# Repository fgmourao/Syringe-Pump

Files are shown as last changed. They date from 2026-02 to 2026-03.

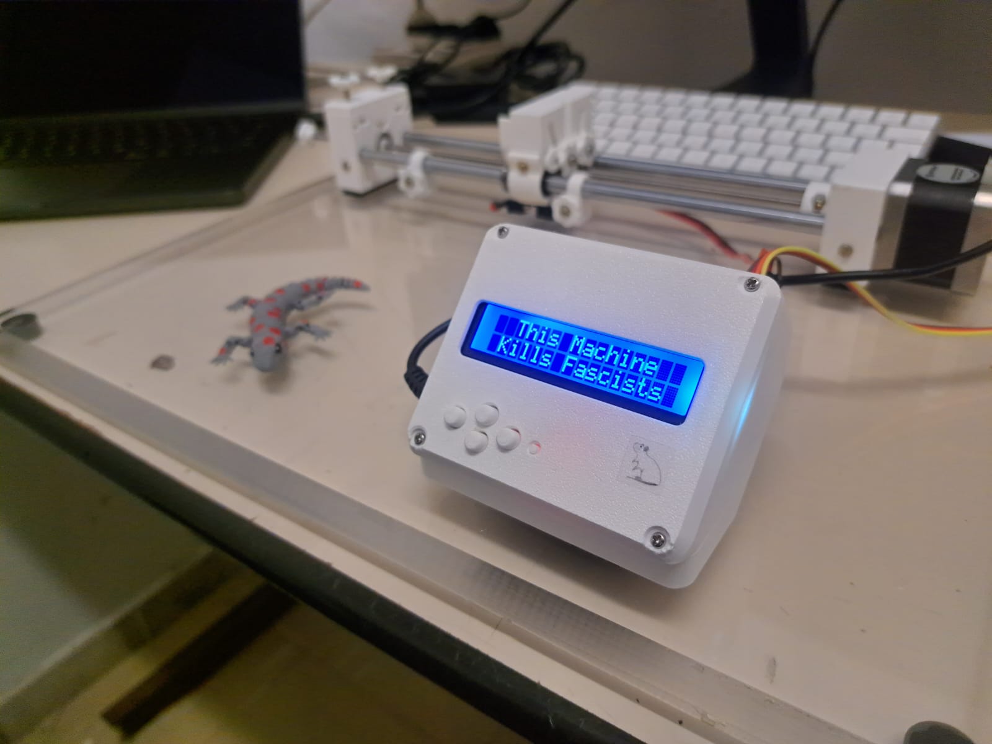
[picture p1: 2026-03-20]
Images/3.jpeg

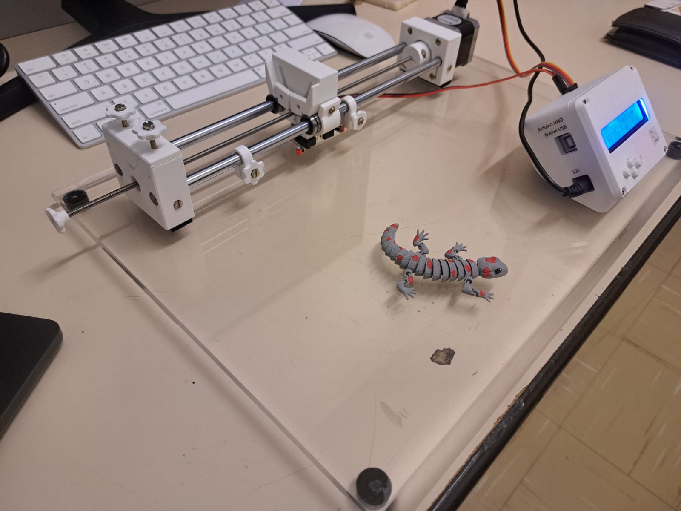
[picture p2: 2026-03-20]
Images/1.jpeg

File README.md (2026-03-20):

# Open-Source Syringe Pump – Modified Version

This firmware is a modified version of the open-source syringe pump originally developed by **Andrey Samokhin** (v0.9a, March 1, 2020).

> **Original project:** [mass-spec.ru/projects/diy/syringe_pump/eng](https://www.mass-spec.ru/projects/diy/syringe_pump/eng/)
> *All credit for the original concept and baseline implementation belongs to the original author.*

The modifications listed below were made targeting improved motion smoothness, manual positional control, and operator safety during microinjection procedures.

Updated: 01/2026 by Flavio Mourao

---

## Change 1 — Lead screw pitch updated

The default lead screw was replaced with a **0.6 mm/revolution** unit, reducing linear displacement per motor step and resulting in smoother, more continuous motion during fine procedures.

| Parameter | Original | Modified |
| :--- | :---: | :---: |
| Lead screw pitch | 2.0 mm/rev | **0.6 mm/rev** |

---

## Change 2 — Manual Positioning Mode (Jog Control)

A dedicated **Positioning** entry was added to the main menu (between *Cycle Mode* and *Settings*), enabling direct real-time control of the syringe position via the existing interface buttons.

### Button mapping

| Button | Action |
| :--- | :--- |
| **UP** | Forward movement (while held) |
| **DOWN** | Backward movement (while held) |
| **LEFT** | Exit positioning mode |
| **RIGHT** | Reset relative position counter ($mm = 0$) |

### Features
* **Press-to-move:** Movement occurs only while a button is actively held.
* **Dual-speed operation:** short press → fine positioning; long press → fast positioning.
* **Power efficiency:** Stepper driver is enabled only during active movement, reducing heat and electrical noise.
* **Endstop safety:** Audible beep when a mechanical limit is reached; movement stops automatically.
* **Real-time feedback:** Relative displacement displayed in millimeters on the LCD.

> **Note:** This mode is intended for manual syringe alignment and fine adjustment prior to automated infusion.

---

## Change 3 — Startup screensaver customized

---

## Change 4 — Start confirmation dialog added

A `confirmStart()` function was introduced to require explicit operator confirmation before any pumping operation begins. After selecting an infusion or refill action, the LCD prompts:

```
Ready to Start?
< NO       YES >
```

* **RIGHT** → confirm and proceed
* **LEFT** → cancel and return to menu

---

## Change 5 — Rounding correction in value calculation

In the original `calculateActualValue()` function, the computed
FLOWRATE and VOLUME values were assigned to `uint32_t` via direct
float-to-integer cast, which always truncates (e.g. `2.9 → 2`).

This was replaced with conventional rounding by adding `0.5` before
the cast (e.g. `(uint32_t)(value + 0.5)`), consistent with the
rounding already applied elsewhere in the original code.

| Location | Original | Modified |
| :--- | :--- | :--- |
| FLOWRATE assignment | `(uint32_t)tempFloat` | `(uint32_t)(tempFloat + 0.5)` |
| VOLUME assignment | `(uint32_t)tempFloat` | `(uint32_t)(tempFloat + 0.5)` |

This reduces cumulative rounding errors in microstep counts,
improving dispensed volume accuracy over repeated operations.

---

## Summary

| # | Change | Scope |
| :---: | :--- | :--- |
| 1 | Lead screw pitch: 2.0 → 0.6 mm/rev | Mechanical + firmware (`MMPER360`) |
| 2 | Manual Positioning Mode (jog control) | Firmware — new function + menu entry |
| 3 | Custom startup screensaver | Firmware — `showScreensaver()` |
| 4 | Start confirmation dialog | Firmware — new `confirmStart()` + `pumpSingly()` |
| 5 | Rounding correction in value calculation | Firmware — `calculateActualValue()` |

---

## Author

Flavio Mourao (mourao.fg@gmail.com)  
Federal University of Minas Gerais, Brazil  

Development started: January 2026  
Last update: March 2026

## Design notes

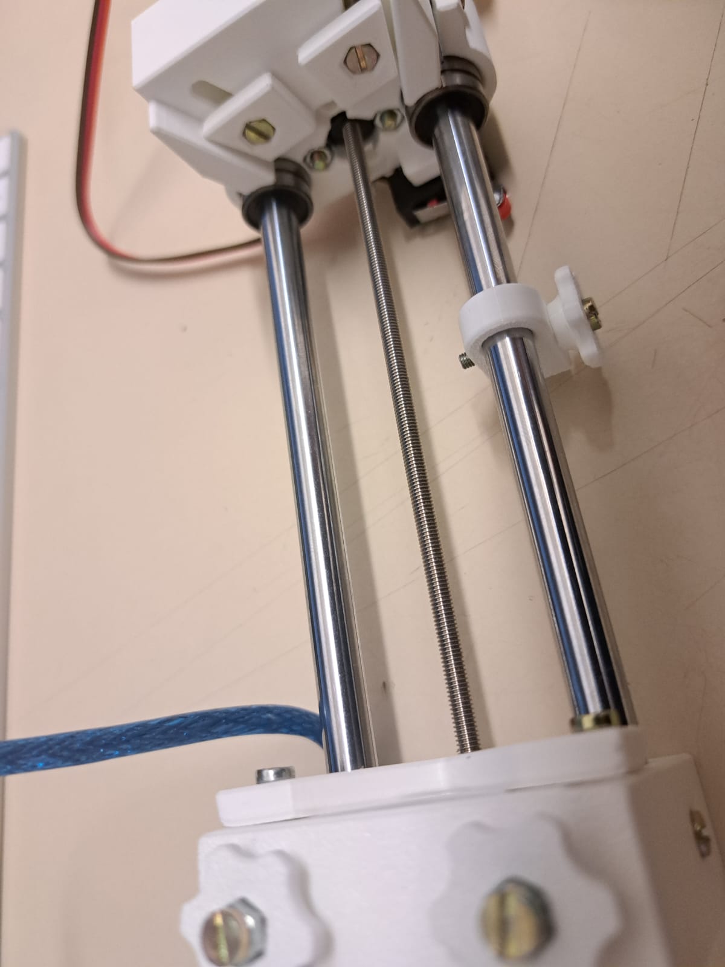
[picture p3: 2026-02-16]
Images/lead_screw_0-6mm.jpeg

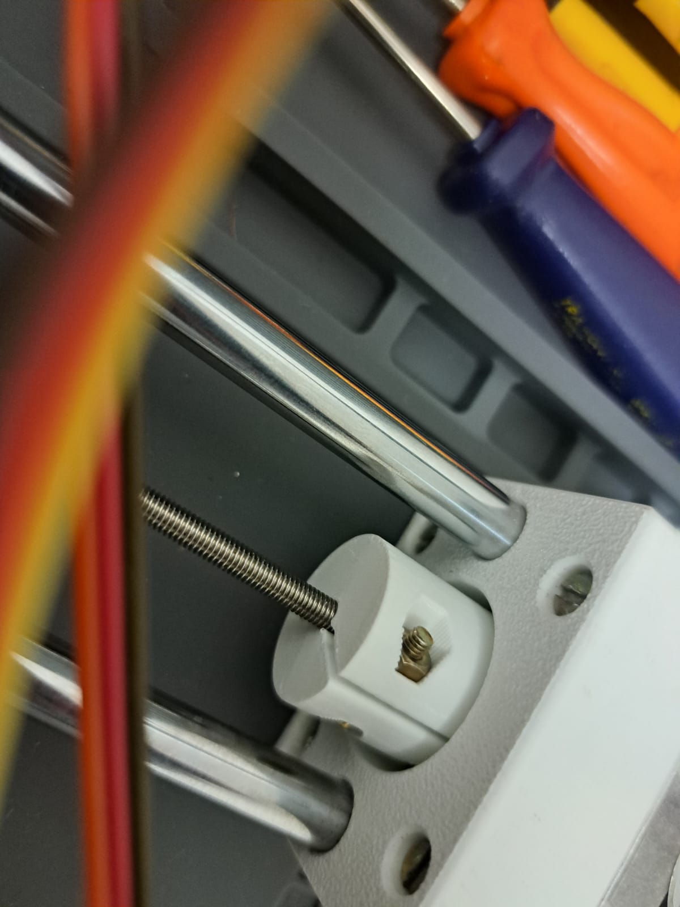
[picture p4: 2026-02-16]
Images/lead_screw_holder_0-6mm.jpeg

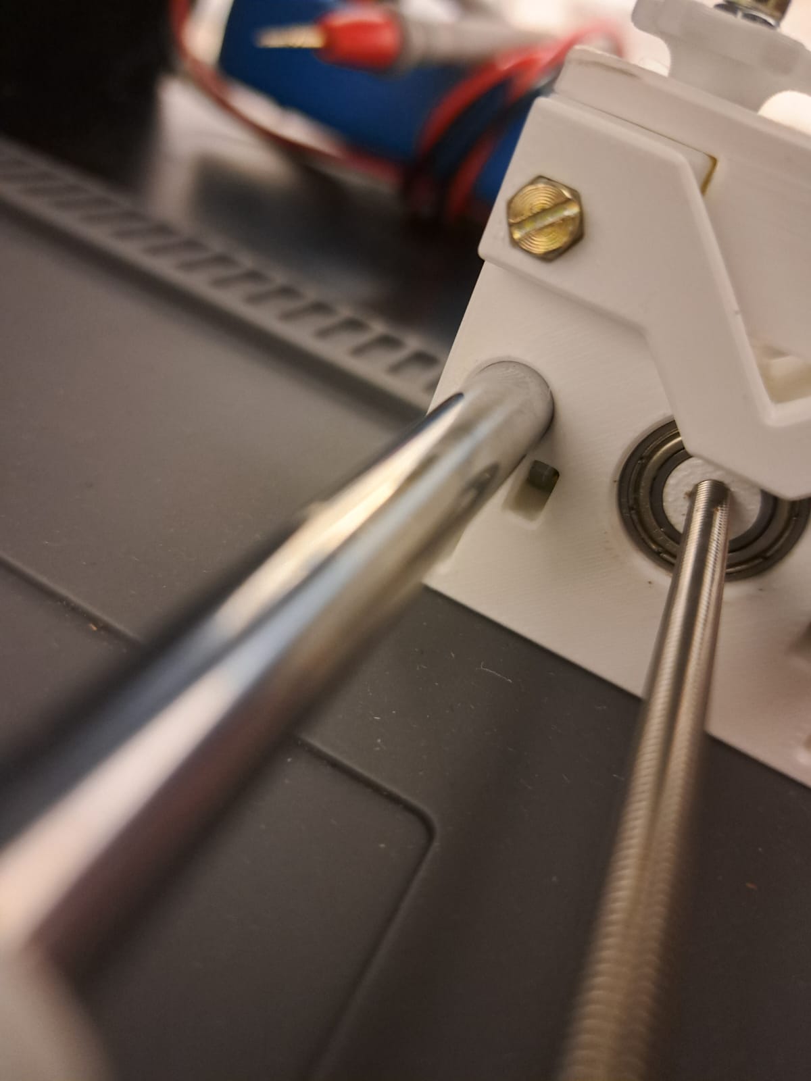
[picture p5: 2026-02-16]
Images/lead_screw_front_adapt.jpeg

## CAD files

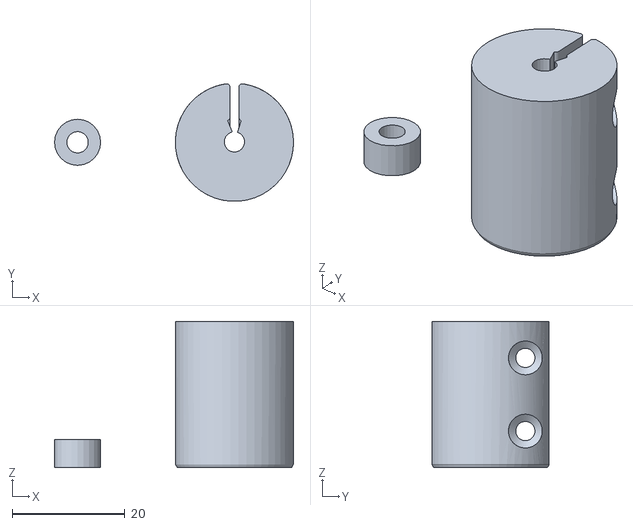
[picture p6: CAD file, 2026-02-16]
3D_/Updates/Flavio_update_adapters_0-6_step_fuse.stl
42.5 x 20.9 x 26.0

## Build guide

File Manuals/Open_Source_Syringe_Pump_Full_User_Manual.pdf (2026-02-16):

# Open-Source Syringe Pump User Manual

Based on the original project by Andrey Samokhin (2020).
Firmware updates and mechanical modifications by Flavio Mourão (2026).

## 1. Overview

This open-source syringe pump is designed for precise liquid delivery and withdrawal, with particular emphasis on laboratory microinjection applications. The system integrates automated pumping modes with a manual positioning (jog) mode, providing both reproducibility and fine user control.

## 2. Hardware Configuration

### Stepper Motor and Drive

The system uses a 200 steps/revolution stepper motor with 16× microstepping, driven by an A4988-compatible driver. The maximum operational speed is 240 RPM.

### Lead Screw

A lead screw with a 0.6 mm/revolution lead was incorporated into the original design to reduce linear displacement per motor step. This modification results in smoother motion and improved controllability during microinjection, while preserving the intrinsic precision of the stepper motor system.

### Endstops

Two mechanical endstops are installed to define the forward (syringe empty) and backward (syringe full) limits, providing hardware-level protection against overtravel.

## 3. User Interface

### Display

A 16×2 LCD is used to display menus, parameters, and real-time operational status.

### Buttons (LCD Keypad Shield)

UP: Navigate up / Forward jog (Positioning mode)
DOWN: Navigate down / Backward jog (Positioning mode) LEFT: Navigate back / Exit positioning mode
RIGHT: Navigate forward / Reset position (Positioning mode) SELECT: Confirm menu item / Edit values

## 4. Menu Structure

Main menu items include: Infuse, Refill, Cycle Mode, Settings, and Positioning.

## 5. Automated Pumping Modes

Infuse Volume: Delivers a defined volume at a specified flow rate. Infuse Time: Infuses continuously for a defined duration.
Refill Volume: Withdraws a defined volume at a specified flow rate. Full Refill: Withdraws until the backward endstop is reached. Cycle Mode: Alternates between infusion and refill automatically.

## 6. Manual Positioning Mode (Jog Control)

The Positioning mode is intended for syringe alignment, manual calibration, and fine positioning prior to microinjection procedures.

### Controls

UP: Forward movement (while pressed) DOWN: Backward movement (while pressed) LEFT: Exit positioning mode
RIGHT: Reset position to zero (mm = 0)

### Behavior

Movement occurs only while a button is pressed; releasing the button immediately stops the motor. Two speeds are automatically selected based on press duration: short press for fine positioning and long press for fast movement.

### Position Display

The LCD displays the relative linear displacement in millimeters in real time. The position is relative and can be reset at any time using the RIGHT button.

### Endstop Feedback

When a mechanical endstop is reached, motion stops immediately and an audible beep is emitted to notify the user.

## 7. Safety Notes

Always verify syringe parameters before operation. Manual positioning should be performed at low speed near the end of travel. Mechanical endstops provide the primary safety mechanism against overtravel.

## 8. Intended Use

This device is intended for laboratory research applications, including microinjection and controlled fluid delivery. It is not certified for clinical or medical use.

## 9. Version Information

Firmware version: 0.9a
Original project: Andrey Samokhin (2020)
Firmware extensions and mechanical updates: Flavio Mourão (2026)

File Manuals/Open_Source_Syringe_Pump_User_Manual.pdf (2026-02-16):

# Open-Source Syringe Pump – User Manual

Based on the original project by Andrey Samokhin (2020). Firmware updates and mechanical modifications by Flavio Mourão (2026).

## Overview

This open-source syringe pump is designed for precise fluid delivery and withdrawal, with special emphasis on microinjection applications. The system integrates automated pumping modes with a manual positioning (jog) mode.

## Mechanical Configuration

A lead screw with a 0.6 mm/revolution lead was incorporated into the original design to reduce linear displacement per motor step, resulting in smoother motion during microinjection, while preserving the intrinsic precision of the stepper motor system.

## Manual Positioning Mode (Jog Control)

The Positioning mode is intended for syringe alignment, fine manual adjustment, and preparation prior to microinjection procedures.
Controls:
UP: Forward movement (while pressed)
DOWN: Backward movement (while pressed) LEFT: Exit positioning mode
RIGHT: Reset position to zero (mm = 0)

## Features

- Movement occurs only while a button is pressed
- Two automatic speeds (short press = fine, long press = fast)
- Stepper driver enabled only during motion
- Audible feedback when a mechanical endstop is reached
- Real-time display of relative displacement in millimeters

## Safety Notes

Mechanical endstops provide hardware-level protection against overtravel. Manual positioning should be performed carefully near the end of syringe travel.

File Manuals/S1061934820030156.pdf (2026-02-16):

ISSN 1061-9348, Journal of Analytical Chemistry, 2020, Vol. 75, No. 3, pp. 416–421. © Pleiades Publishing, Ltd., 2020. Russian Text © The Author(s), 2020, published in Zhurnal Analiticheskoi Khimii, 2020, Vol. 75, No. 3, pp. 281–287.

## Syringe Pump Created Using 3D Printing Technology and Arduino Platform

A. S. Samokhin*
Lomonosov Moscow State University, Chemistry Department, Moscow, 119991 Russian *e-mail: andrey.s.samokhin@gmail.com

Received December 24, 2018; revised September 1, 2019; accepted September 1, 2019

Abstract—An open-source syringe pump has been developed for use in the analytical laboratory. Most pump parts are made on a 3D printer. Other parts (lead screw, guide rods, stepper motor, bearings, electronic components) are purchased in specialized stores. The control panel is based on the Arduino UNO. Device interaction, any settings changes, and operating mode selection are carried out using the LCD Keypad Shield (no computer connection required). The program for the microcontroller is written in Arduino IDE. Assembling the syringe pump takes several hours and requires almost no soldering. Universal clamp allows installing any syringe with a diameter of 6 to 25 mm. The syringe pump can both infuse the liquid and refill the empty syringe. To evaluate the analytical characteristics, a 10-mL glass syringe (Kloehn) was used. The dispensed volume was 1 and 5 mL. The systematic error was less than 0.1%, and the random one was less than 3 μL. Project files are available at: http://www.mass-spec.ru/projects/diy/syringe_pump/eng/.

Keywords: syringe pump, open-source, open-source hardware, Arduino, 3D printing
DOI: 10.1134/S1061934820030156

The Arduino platform was created through the
efforts of enthusiasts just over 10 years ago. It lowers the barrier to entry for embedded programming and the development of electronic devices. Around the same time, the first prototype of the at-home 3D printer was assembled and tested (it printed objects from plastic using fused filament fabrication technology). Nowadays there are several platforms for the development of electronic devices (besides the Arduino there are, for example, the Netduino or the Raspberry Pi). In addition, at-home 3D printers are widespread, both due to a large number of open-source printer projects and the start of mass production. There are online repositories of 3D models for printing and projects based on the Arduino or the Raspberry Pi on the Internet. Most models and projects are open-source, therefore it is possible not only to reproduce them, but also make some changes to the source code or 3D model, when necessary.

A large number of projects have been developed for use in chemical and biochemical laboratories. On the Internet and on the pages of scientific journals everyone can find projects of glass vial and Eppendorf tube holders [1, 2], centrifuges [3, 4], magnetic stirrers [5– 7], laboratory shakers [8], peristaltic pumps [9–11], pH meters [12–14], automatic titrators [15, 16], data acquisition devices [17, 18], electronic burettes [19], micropipettes [20–22], colorimeters [23–25], detectors for chromatography and capillary electrophoresis

[26, 27], automated systems for sample preparation and analysis [28–30], autosamplers for gas chromatography [31], syringe pumps [32–45] and some other devices.
We have developed yet another open-source project of the syringe pump, that was designed for use in the analytical laboratory. We believe that the DIY syringe pump should meet a number of requirements in order to be a good alternative to commercial devices. Firstly, it should be a standalone device. All parameters (including the volume of the syringe) should be changed autonomously without a computer or mobile device. Secondly, the syringe holder should be multi-purpose so that various volume syringes can be quickly installed or replaced. Thirdly, the flow rate should be widely varied and strictly controlled during operation. Moreover, in order to simplify the replication of the project, the control panel should be assembled using commercially available modules (in this case, it is not necessary to produce a custom circuit board). None of the previously proposed projects of syringe pumps (Table 1) satisfies all of the above requirements. This was the motivation for the development of a new device.

SYRINGE PUMP DESIGN
A general view of the syringe pump and the electrical circuit are shown in Figs. 1 and 2, respectively. A complete list of parts is presented in Table 2.

ANALYTICAL INSTRUMENTS

JOURNAL OF ANALYTICAL CHEMISTRY | Vol. 75 | No. 3 | 2020
SYRINGE PUMP CREATED USING 3D PRINTING TECHNOLOGY | 417

Table 1. Description of syringe pumps presented in the literature

Manufacturing
process

Universal mount and

| quick syringe replacement | Control board | Custom
| | | circuit board | Syringe pump control
| | | | method | Reference
3D printing | No | Arduino Nano | No | Serial port | [32]
3D printing | No | Board with
| | ATmega 328P | Yes | Serial port | [33]
Handmade | No | Arduino Nano | No | Serial port | [34]
3D printing | No | – | – | – | [35]
3D printing | No | Arduino Uno | No | Autonomous control (using
| | | | buttons and display) | [36, 37]
3D printing | No | Arduino Uno | No | Serial port or Android
| | | | device (connected to the
| | | | syringe pump via bluetooth) | [38]
Acrylic laser cutting | No | Board with
ATmega 328P
| Yes | Autonomous control (using buttons and display) | [39]
3D printing | Yes
(only plastic syringes can be installed)
Arduino Uno | No | Serial port | [40]
3D printing | No | Raspberry Pi | No | Web Interface | [41]
3D printing | No | Arduino Uno | No | NI LabVIEW Interface | [42]
Handmade | Yes | Raspberry Pi | No | Autonomous control (key- board, mouse and monitor are required) or remote con- trol (for example, via SSH) | [43]
3D printing | No | Arduino Uno | No | Serial port | [44]
3D printing | No | Raspberry Pi | No | Autonomous control (using touch screen) | [45]

The syringe is mounted on the front support 1
using the top 3, and side 4 holders. The two top syringe holders 3 were designed for syringes with outer diameters of 6–12 and 12–25 mm. To refill the syringe automatically, plunger flange should be fixed on the carriage 10. The target volume is delivered by the movement of the carriage 10 along the guide rods 5. Two endstop switches 11 are mounted on the carriage
10. Limit stops 6 allow to set the acceptable travel limits of the carriage 10 and the syringe plunger. The carriage 10 is moved by rotating the lead screw 8, which is connected coaxially to the stepper motor 18 by means of a coupling 16. Such design is used in most open-source projects. On the other hand, in most commercially available devices, the lead screw and motor are connected by a gearbox or belt drive. Step-down gearing reduces angular velocity and increases torque. Nevertheless, even a coaxial connection provides accurate fluid delivery and sufficient pressure on the syringe plunger. In our design, the carriage moves 1 mm for 1600 micro-steps (when 2 mm thread pitch is installed and 1/16 micro-stepping mode is used). The carriage applies a linear force of at least 70 N to the plunger (when moving at a speed of 20 mm/min).

Linear force can be increased by using a lead screw with a smaller pitch.
The syringe pump is controlled by the Arduino UNO 21. LCD Keypad Shield 23 is used for input/output purposes. It consists of the LCD1602 display and 6 buttons. The LCD Keypad Shield is plugged into the Arduino UNO board (no soldering is required). The stepper motor is controlled by the A4988 24 driver, which is plugged into the expansion board 25. The stepper motor operates in 1/16 micro-stepping mode (all three switches on the expansion board are set to ON). Active buzzer 26 is used to make a sound. All electronic components are housed in a plastic case, which consists of a base 19 and a cover 20. Five buttons 21 are used to control the device.
The firmware was written by us in C using the Arduino IDE. The user interacts with the device using a multi-level menu that allows to change the volume of the syringe or the units of measure (time, volume, flow rate), select the operating mode of the syringe pump and set all the necessary parameters (volume or time of infusion, flow rate). The values of all parameters are stored in non-volatile memory. When changing units, the values of all variables are recalculated automatically. The flow rate and its consistency are achieved by

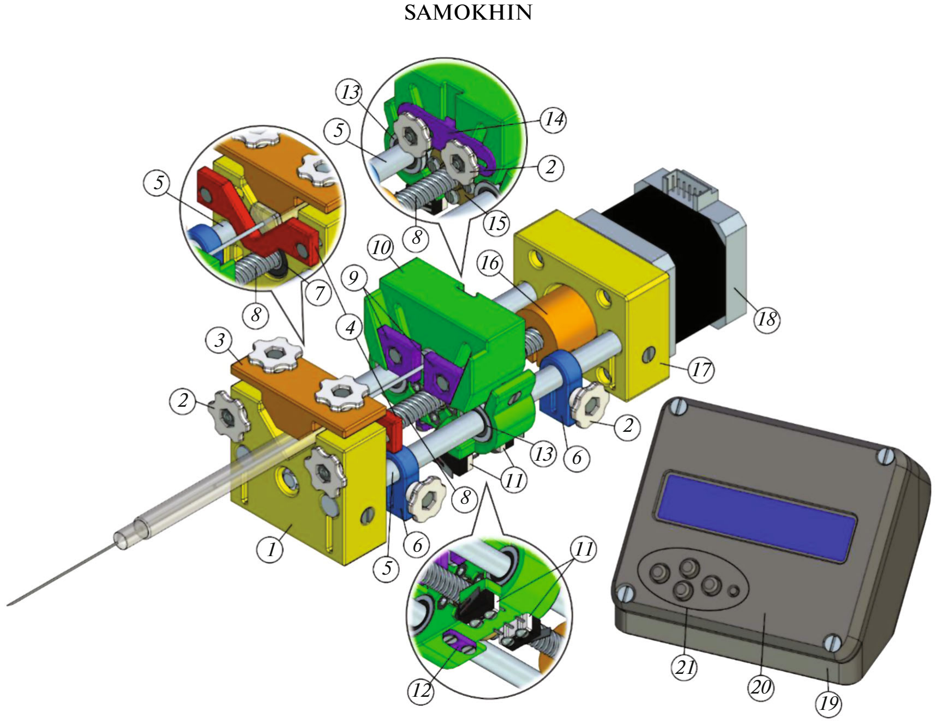
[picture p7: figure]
SAMOKHIN

sending pulses to the stepper motor driver. Pulses are generated by Timer1 interrupts. It should be emphasized that not all values of the volume and flow rate selected by the user can be implemented (due to discreteness). In this case, the closest allowed value is calculated and displayed.
Three operating modes of the syringe pump are implemented. In ‘Infuse’ mode, fluid is squeezed out of the syringe at a strictly controlled flow rate. The user can set either the fluid volume or infusion time. In ‘Refill’ mode, the syringe is filled with fluid. In ‘Cycle’ mode, the direction of the plunger movement changes automatically when the endstop switch is triggered.
Project files are distributed under the Creative Commons BY-SA 4.0 license [46] and are available at: http://www.mass-spec.ru/projects/diy/syringe_pump/eng/. Detailed instructions are available at the same website.

CALIBRATION OF THE SYRINGE PUMP

The fluid was delivered using the DIY syringe pump developed in this work and two commercially available devices: HA 11 Plus (Harvard Apparatus) and KDS 100 (KD Scientific). The same Kloehn 4010 (Kloehn) glass syringe with a volume of 10 mL was used in all cases. The weighing was carried out using a

Vibra HTR-220CE analytical balance (Shinko Denshi) with a verification scale interval of 1 mg.

The syringe was calibrated by gravimetric determination of its inner diameter. To simplify the subsequent calculations, the inner diameter of the syringe

Fig. 1. General view of the DIY syringe pump.

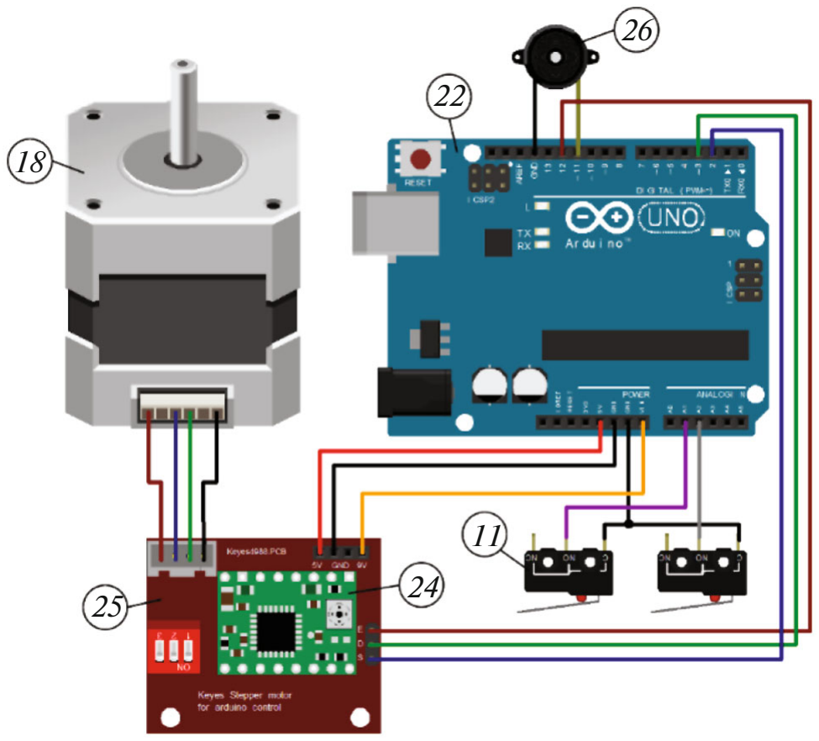
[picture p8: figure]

Fig. 2. Electrical circuit.

was set to 11.284 mm (being expressed in mL the infusion volume is numerically equal to the distance traveled by the carriage and expressed in cm). The syringe was completely filled with double distilled water and installed in the syringe pump. A small volume of water (0.5–1 mL) was wasted. The carriage was then moved with a linear velocity of 0.2 mm/s over a distance of 5 cm (this corresponded to approximately 8.3 mL of the Kloehn 4010 syringe). Water was collected in a 20 mL glass vial and weighed on the analytical balance. To minimize evaporation during infusion and weighing the vial was closed with a screw cap with a small hole. The described procedure was repeated 5 times independently for each syringe pump. The inner diameter was calculated by the formula:

in | 2 | 2 | , π | 5π
V | mZ D
L = | =

where Din is the inner syringe diameter, cm; V is the delivered volume, mL; L is the distance moved by the plunger, cm; m is the mass of water, g; Z is the correction factor (ISO 8655-6) depending on temperature and air pressure, mL/g.
The inner diameter of the Kloehn 4010 syringe, determined gravimetrically using the DIY syringe pump, HA 11 Plus and KDS 100 was 14.551 ± 0.006, 14.580 ± 0.006 and 14.576 ± 0.007 mm respectively (n = 5, P = 0.95). The average diameter determined by the DIY syringe pump was significantly different from the values obtained using commercial devices. Apparently, the observed differences were caused by the difference between the actual and nominal pitch of the lead screw installed in the DIY syringe pump. To minimize the value of the systematic error, device-specific inner diameters were used for each pump.

ANALYTICAL PERFORMANCE
OF THE SYRINGE PUMP
The analytical performance of the syringe pumps was evaluated gravimetrically. The syringe diameter was set equal to the value determined at the calibration stage. The infusion volume was 1 or 5 mL. The infusion rate was 2, 7.5 or 20 mL/min (linear velocity of the carriage was 0.2, 0.74 or 2 mm/s, respectively). At a particular flow rate the target volume was delivered 8 times. The systematic error was calculated as the difference between the mean delivered volume and the desired target volume. The random error was expressed by the standard deviation.
As can be seen from Table 3, the DIY syringe pump is not inferior to commercial devices in both accuracy and reproducibility. Analytical performance is constant over the entire range of flow rates considered in this study (from 2 to 20 mL/min). The systematic error is less than 0.1%; the random error is less than 3 μL (for 10 mL syringe).
As can be seen from Table 2, the cost of all syringe pump parts is less than $ 100 (when parts are purchased in Chinese online stores, the cost is less than $ 50). Assembling the syringe pump takes several hours and requires almost no soldering. The use of widespread components and the availability of detailed instructions make it easy to reproduce this project.

* * *
The open-source syringe pump has been developed. All project files are distributed under the CC BY-SA 4.0 and are available at: http://www.mass-spec.ru/projects/diy/syringe_pump/eng/. The syringe pump developed in this study is not inferior to many commercially available devices in its functionality and analytical performance. Open-source code allows anyone to make changes and solve specific problems. The relatively low cost and ease of assembly make it

Table 2. Part list

* Parts marked with an asterisk are designed by us and printed on a 3D printer.
** The cost of 3D printed plastic parts (infill is 50%, production cost is assumed to be equal to 42 USD/kg) or the price range for commercially available parts (offered by Russian online stores).
Part # | Part name | Cost**, USD
1 | Front support* | 1.1
2 | Hand knob* | 0.03 × 8
3 | Top syringe holder* | 0.3
4 | Side syringe holder* | 0.2
5 | Guide rod (D = 8 mm) | (2.5–4.2) × 2
6 | Limit stop* | 0.08 × 2
7 | Bearing (688zz) | 0.5–0.8
8 | Lead screw (Т8) | 3.3–5.0
9 | Plunger holders* | 0.08
10 | Carriage* | 1.2
11 | Endstop switch | (0.6–0.8) × 2
12 | Wire holder* | 0.02
13 | Linear bearing (LM8SUU) | (1.0–3.3) × 2
14 | Slider* | 0.05
15 | Lead screw nut (Т8) | 1.7–3.3
16 | Coupling* | 0.3
17 | Back support* | 1.3
18 | Stepper motor Nema 17 | 11.7–20
19 | Case (base)* | 2.1
20 | Case (cover)* | 0.7
21 | Buttons * | 0.05
22 | Arduino UNO clone | 6.7–10.0
23 | LCD Keypad shield | 5.0–10.0
24 | Stepper motor driver A4988 | 2.5–6.6
25 | Control shield for A4988 | 3.3–6.6
26 | Active buzzer | 0.5–0.8

SAMOKHIN

possible to implement this project in any analytical or teaching laboratory.

REFERENCES

1. Holder (stand) for 20/30 gas chromatography (GC) vials. http://www.thingiverse.com/thing:399955. Accessed December 13, 2018.
2. Modular Eppendorf tube rack V2.0. http://www.thingiverse.com/thing:2794834. Accessed December 13, 2018.
3. F.Lab’s | DIYbio | centrifuge. | http://www.thingi-
verse.com/thing:1175393. Accessed December 13, 2018.
4. El-cheapo | tabletop | minifuge. | http://www.thingi-
verse.com/thing:33818. Accessed December 13, 2018.
5. Magnetic stirrer from a 80-mm fan. http://www.thingiverse.com/thing:1663540. Accessed December 13, 2018.
6. F.Lab’s DIYbio magnetic stirrer. http://www.thingiverse.com/thing:1175415. Accessed December 13, 2018.
7. Mercer, C. and Leech, D., J. Chem. Educ., 2017, vol. 94, no. 6, p. 816.
8. Dhankani, K.C. and Pearce, J.M., HardwareX, 2017, vol. 1, p. 1.
9. Low-cost | peristaltic | pump. | http://www.thingi-
verse.com/thing:254956. Accessed December 13, 2018.
10. Peristaltic | Pump | Improved | for | Nema | 17.
http://www.thingiverse.com/thing:1134817. Accessed December 13, 2018.
11. iGem | Hardware. | http://2017.igem.org/
Team:Aachen/Hardware. | Accessed | December 13,
2018.
12. Kubinova, S. and Slegr, J., J. Chem. Educ., 2015, vol. 92, no. 10, p. 1751.
13. Papadopoulos, N.J. and Jannakoudakis, A., J. Chem. Educ., 2016, vol. 93, no. 7, p. 1323.
14. Jin, H., Qin, Y., Pan, S., Alam, A.U., Dong, S., Ghosh, R., and Deen, M.J., J. Chem. Educ., 2018, vol. 95, no. 2, p. 326.
15. Famularo, N., Kholod, Y., and Kosenkov, D., J. Chem. Educ., 2016, vol. 93, no. 1, p. 175.
16. Milanovic, J.Z., Milanovic, P., Kragic, R., and Kostic, M., PLoS One, 2018, vol. 13, no. 3, e0193744.
17. Grinias, J.P., Whitfield, J.T., Guetschow, E.D., and Kennedy, R.T., J. Chem. Educ., 2016, vol. 93, no. 7, p. 1316.
18. Walkowiak, M. and Nehring, A., J. Chem. Educ., 2016, vol. 93, no. 4, p. 778.
19. Cao, T., Zhang, Q., and Thompson, J.E., J. Chem. Educ., 2015, vol. 92, no. 1, p. 106.
20. Biropette: Customisable, high precision pipette. http://www.thingiverse.com/thing:255519. Accessed December 13, 2018.
21. Bravo-Martínez, J., HardwareX, 2018, vol. 3, p. 110.
22. Brennan, M.D., Bokhari, F.F., and Eddington, D.T., Micromachines, 2018, vol. 9, no. 4, p. 191.
23. Anzalone, G., Glover, A., and Pearce, J., Sensors, 2013, vol. 13, no. 4, p. 5338.
24. McClain, R.L., J. Chem. Educ., 2014, vol. 91, no. 5, p. 747.
25. Wittbrodt, B.T., Squires, D.A., Walbeck, J., Campbell, E., Campbell, W.H., and Pearce, J.M., PLoS One, 2015, vol. 10, no. 8, p. e0134989.
26. Prikryl, J. and Foret, F., Anal. Chem., 2014, vol. 86, no. 24,
p. 11951.
27. Cecil, F., Zhang, M., Guijt, R.M., Henderson, A., Nesterenko, P.N., Paull, B., Breadmore, M.C., and Macka, M., Anal. Chim. Acta, 2017, vol. 965, p. 131.
28. Carvalho, M.C. and Eyre, B.D., Methods Oceanogr., 2013, vol. 8, p. 23.
29. Hsieh, K.-T., Liu, P.-H., and Urban, P.L., Anal. Chim. Acta, 2015, vol. 894, p. 35.

Table 3. The systematic and the random errors (n = 8)

* The maximum flow rate of HA 11 Plus is 7.8 mL/min. ** The maximum flow rate of KDS 100 is 2.1 mL/min

Syringe pump | Flow rate,
| mL/min | Volume, mL
Systematic error | Random error
| | | μL | % | μL | %
DIY syringe pump | 2 | 1 | –0.7 | –0.07 | 1.2 | 0.12
| | 5 | –1.3 | –0.03 | 2.2 | 0.04
| 7.5 | 1 | –0.3 | –0.03 | 0.7 | 0.07
| | 5 | –3.4 | –0.07 | 2.5 | 0.05
| 20 | 1 | –0.7 | –0.07 | 2.1 | 0.21
| | 5 | –2.2 | –0.04 | 1.0 | 0.02
HA 11 Plus* | 2 | 1 | 4.0 | 0.40 | 0.9 | 0.09
| | 5 | 0.2 | 0.003 | 1.5 | 0.03
| 7.5 | 1 | 4.8 | 0.48 | 1.0 | 0.10
| | 5 | 2.6 | 0.05 | 2.5 | 0.05
KDS 100** | 2 | 1 | –0.8 | –0.08 | 1.2 | 0.12
| | 5 | –3.3 | –0.07 | 1.3 | 0.03

30. Chen, C.-L., Chen, T.-R., Chiu, S.-H., and Urban, P.L., Sens. Actuators, B, 2017, vol. 239, p. 608.
31. Carvalho, M.C. and Murray, R.H., HardwareX, 2018, vol. 3, p. 10.
32. 3D-Printed syringe pump rack. http://www.instructables.com/id/3D-Printed-Syringe-Pump-Rack/. Accessed December 13, 2018.
33. Patrick, | W., | Open | source | syringe | pump.
http://fab.cba.mit.edu/classes/863.13/people/wildebeest/projects/final/index.html. Accessed December 13, 2018.
34. Connelly, B., Trying to make the worlds cheapest sy-
ringe | pump/linear | drive. | http://www.billconnel-
ly.net/?p=176. Accessed December 13, 2018.
35. Syringe | pump | mechanicals. | https://publi-
clab.org/notes/JSummers/12-30-2014/syringe-pumpmechanicals. Accessed December 13, 2018.
36. Ultra-low flow rates with DIY syringe pumps. http://www.thepulsar.be/article/ultra-low-flow-rateswith-diy-syringes-pumps/. Accessed December 13, 2018.
37. Arduino controller for our low-cost syringe pump. http://www.thepulsar.be/article/arduino-controllerfor-our-low-cost-syringe-pump/. Accessed December 13, 2018.
38. Croatt | Research | Group. | Flow | Chemistry.
https://chem.uncg.edu/croatt/flow-chemistry/. | Ac-
cessed December 13, 2018.
39. Syringe pump. https://karpova-lab.github.io/syringe-pump/index.html. Accessed December 13, 2018.
40. Poseidon system: Open source syringe pumps and microscope for laboratories. https://github.com/pachterlab/poseidon. Accessed December 13, 2018.
41. Wijnen, B., Hunt, E.J., Anzalone, G.C., and Pearce, J.M., PLoS One, 2014, vol. 9, no. 9, e107216.
42. Ryzhov, O.A., Molodoi Uchenyi, 2015, no. 11, p. 425.
43. Cubberley, M.S. and Hess, W.A., J. Chem. Educ., 2017, vol. 94, no. 1, p. 72.
44. LeSuer, R.J., Osgood, K.L., Stelnicki, K.E., and Mendez, J.L., HardwareX, 2018, vol. 4, e00038.
45. Garcia, V.E., Liu, J., and DeRisi, J.L., HardwareX, 2018, vol. 4, e00027.
46. Creative Commons. https://creativecommons.org/licenses/by-sa/4.0/. Accessed December 13, 2018.

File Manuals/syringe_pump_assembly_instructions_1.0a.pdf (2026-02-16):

# Open-Source Syringe Pump

(developed by Andrey Samokhin in 2018)

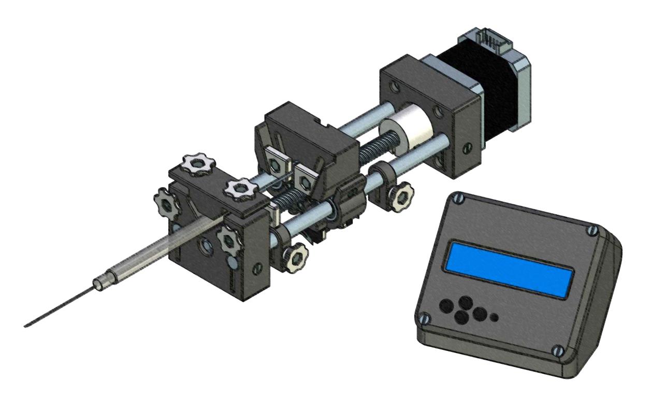
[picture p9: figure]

# Assembly Instructions

(Version 1.0a)

STL-files and "firmware" are available at http://www.mass-spec.ru/projects/diy/syringe_pump/eng/
Project files are distributed under CC BY-SA 4.0 license

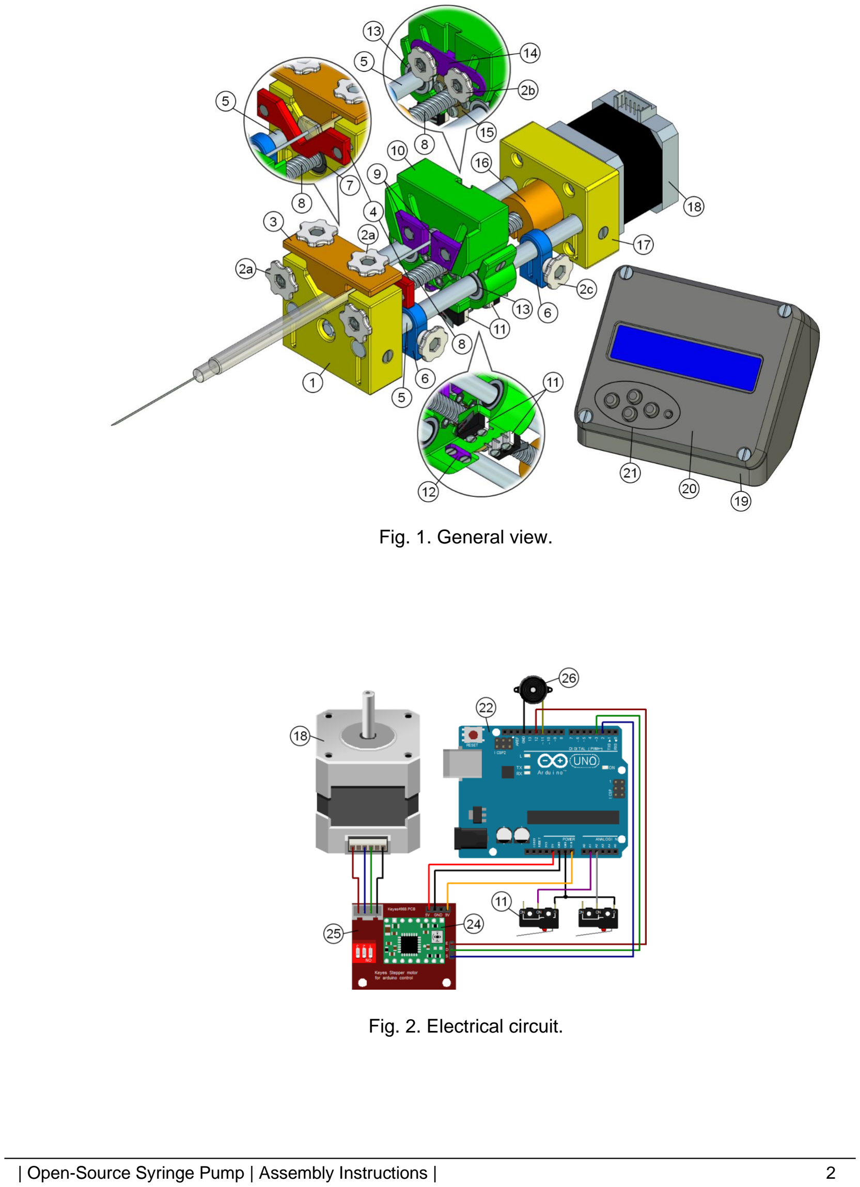
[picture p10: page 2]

| Open-Source Syringe Pump | Assembly Instructions | | 2

Fig. 1. General view.

Fig. 2. Electrical circuit.

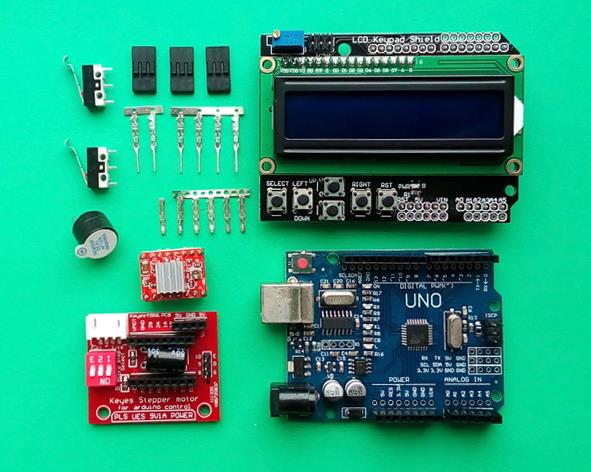
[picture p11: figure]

Fig. 3. Electronic components.

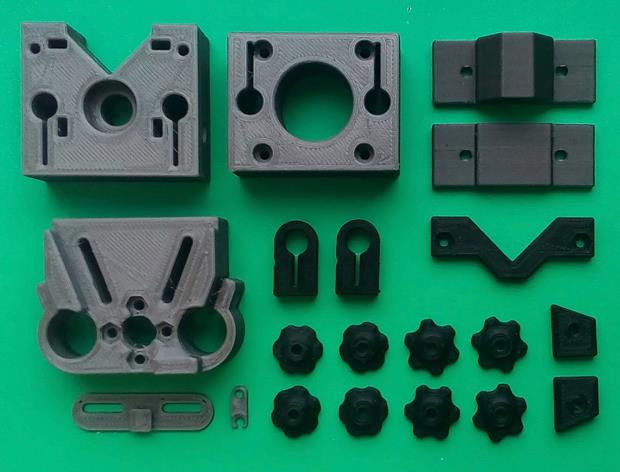
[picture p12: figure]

Fig. 4. Plastic parts made on 3D printer.

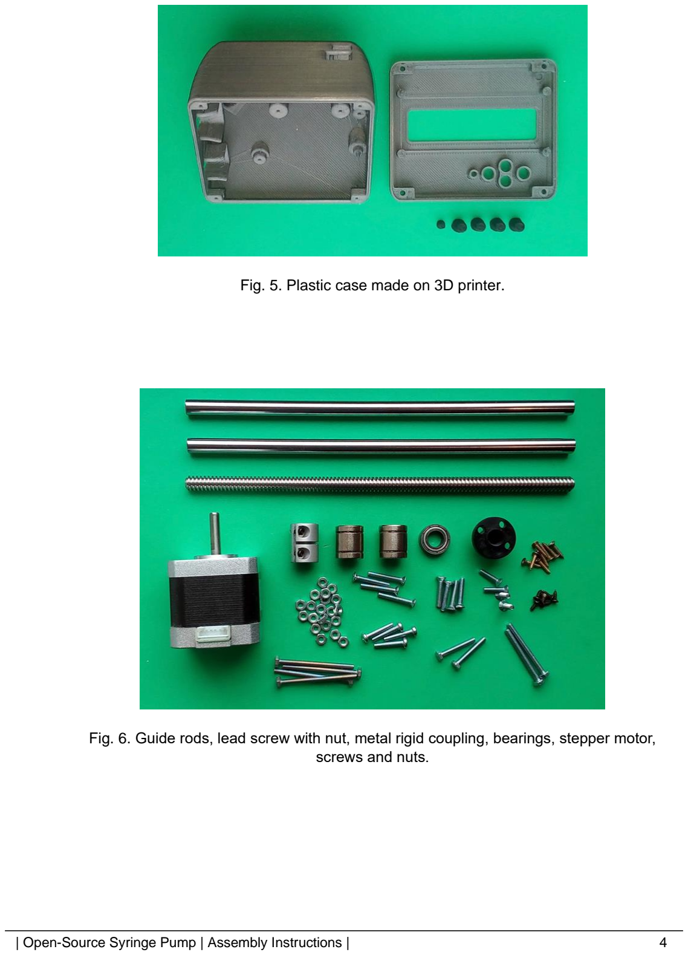
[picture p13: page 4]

Fig. 5. Plastic case made on 3D printer.

Fig. 6. Guide rods, lead screw with nut, metal rigid coupling, bearings, stepper motor, screws and nuts.

| Open

-Source Syringe Pump | Assembly Instructions |
5

Table 1. Part list.

PART # | PART NAME Front Support | QTY 1 1
2a | Hand Knob (9 mm) | 4
2b | Hand Knob (8 mm) | 2
2c | Hand Knob (7 mm) | 2
3 | Top Syringe Holder | 1
4 | Side Syringe Holder | 1
5 | Guide Rod (D=8 mm) | 2
6 | Limit Stop | 2
7 | Bearing 688ZZ | 1
8 | Lead Screw (T8) | 1
9 | Plunger Holders | 1
10 | Carriage | 1
11 | Endstop Switch | 2
12 | Wire Holder | 1
13 | Linear Bearing (LM8SUU) | 2
14 | Slider | 1
15 | Lead Screw Nut (T8) | 1
16 | Coupling | 1
17 | Back Support | 1
18 | Stepper Motor (NEMA 17) | 1
19 | Case (Base ) | 1
20 | Case (Cover ) | 1
21 | Buttons | 1
22 | Arduino UNO | 1
23 | LCD Keypad Shield | 1
24 | Stepper Motor Driver (A4988) | 1
25 | Control Shield for A4988 | 1
26 | Active Buzzer (D=12 mm) | 1
27 | Nut M3 | 20
28 | Countersunk Screw M3x12 | 4
29 | Countersunk Screw M3x14 | 4
30 | Countersunk Screw M3x20 | 4
31 | Pan Head Screw M3x16 | 4
32 | Bolt M3x20 | 2
33 | Bolt M3x25 | 2
34 | Bolt M3x35 | 4
35 | Self -tapping Screw 2x8 | 6
36 | Self -tapping Screw 2x10 | 8
37 | Dupont Connector (Female) | 6
38 | Dupont Connector (Male) | 6
39 | Dupont Housing (3P) | 3
40 | Connector Wires | –
41 | Power Supply (12 V, 2 A) | 1

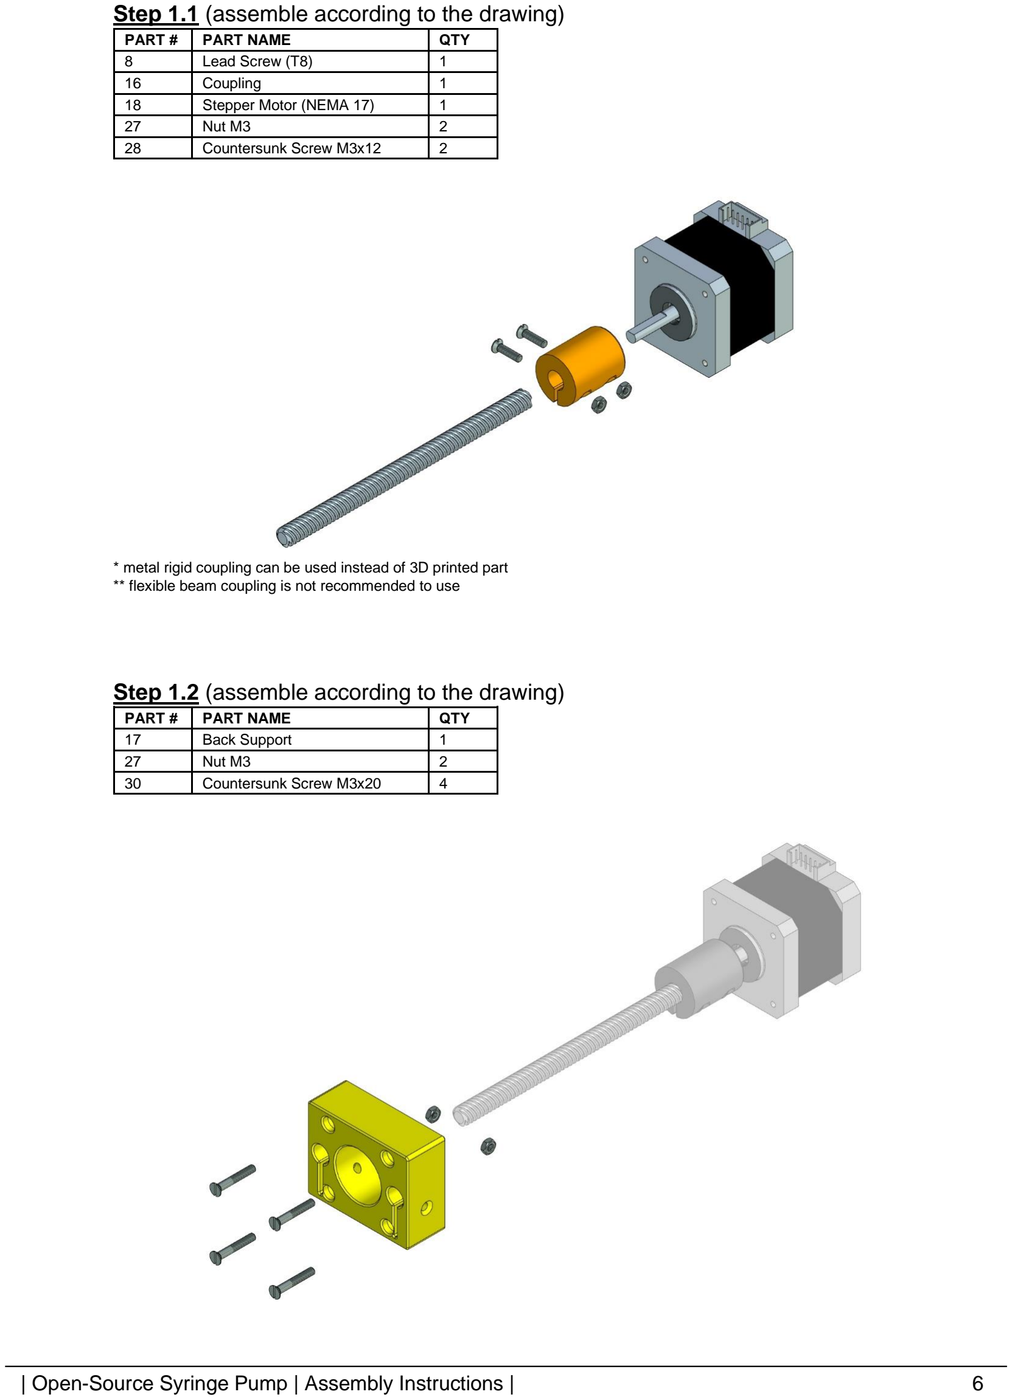
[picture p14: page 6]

Step 1.1 (assemble according to the drawing)
PART # | PART NAME | QTY
8 | Lead Screw (T8) | 1
16 | Coupling | 1
18 | Stepper Motor (NEMA 17) | 1
27 | Nut M3 | 2
28 | Countersunk Screw M3x12 | 2

* metal rigid coupling can be used instead of 3D printed part ** flexible beam coupling is not recommended to use

Step 1.2 (assemble according to the drawing)
PART # | PART NAME | QTY
17 | Back Support | 1
27 | Nut M3 | 2
30 | Countersunk Screw M3x20 | 4

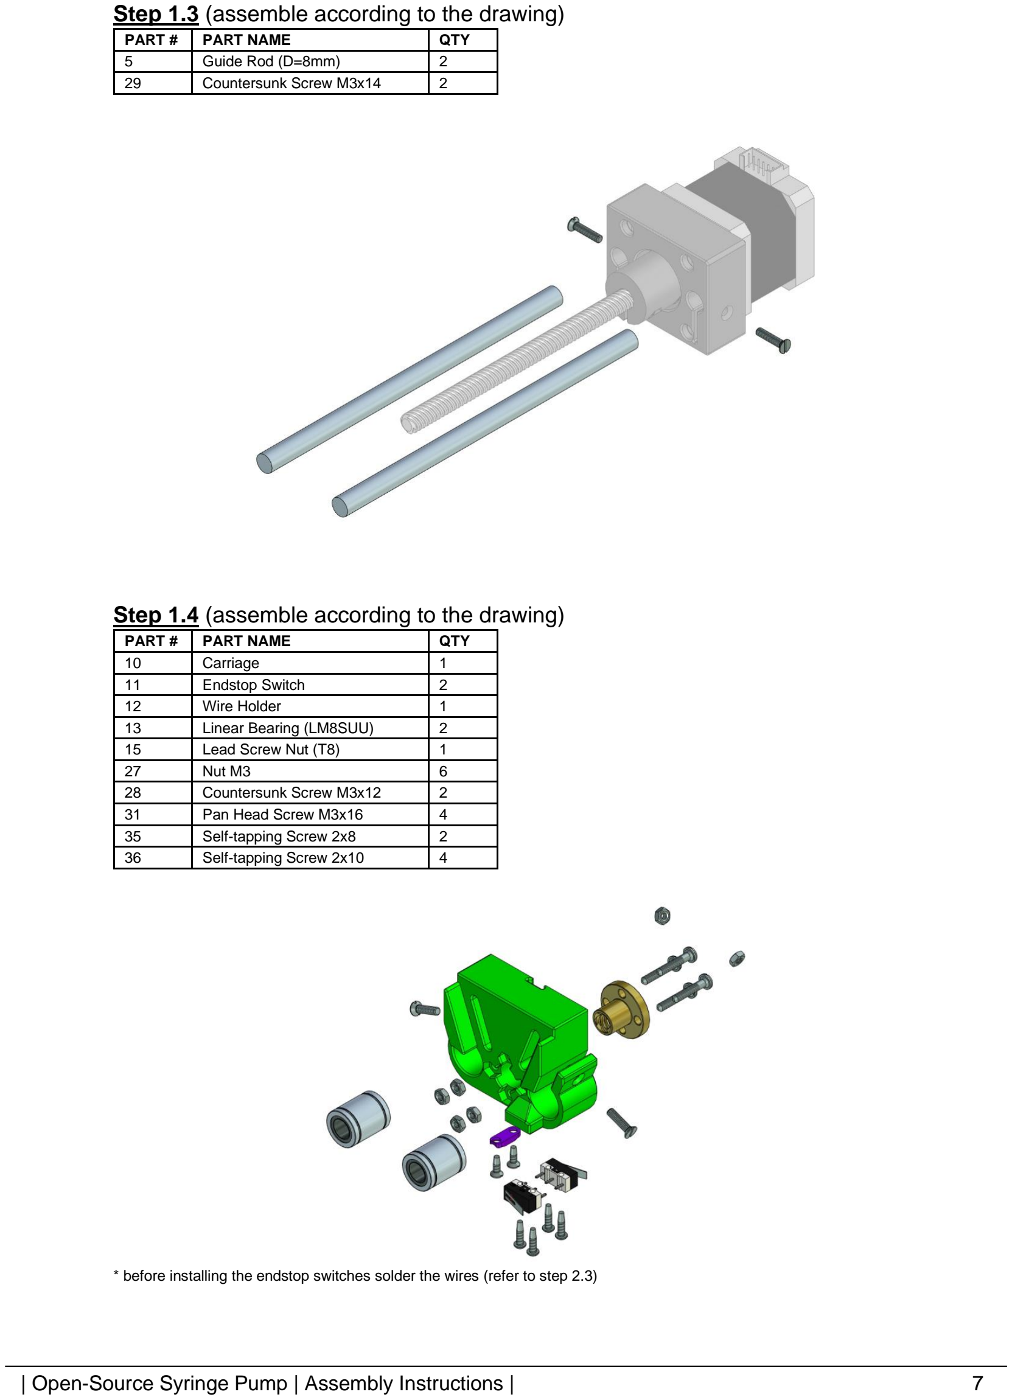
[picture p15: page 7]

Step 1.3 (assemble according to the drawing)
PART # | PART NAME | QTY
5 | Guide Rod (D=8mm) | 2
29 | Countersunk Screw M3x14 | 2
Step 1.4 (assemble according to the drawing)
PART # | PART NAME | QTY
10 | Carriage | 1
11 | Endstop Switch | 2
12 | Wire Holder | 1
13 | Linear Bearing (LM8SUU) | 2
15 | Lead Screw Nut (T8) | 1
27 | Nut M3 | 6
28 | Countersunk Screw M3x12 | 2
31 | Pan Head Screw M3x16 | 4
35 | Self-tapping Screw 2x8 | 2
36 | Self-tapping Screw 2x10 | 4

* before installing the endstop switches solder the wires (refer to step 2.3)

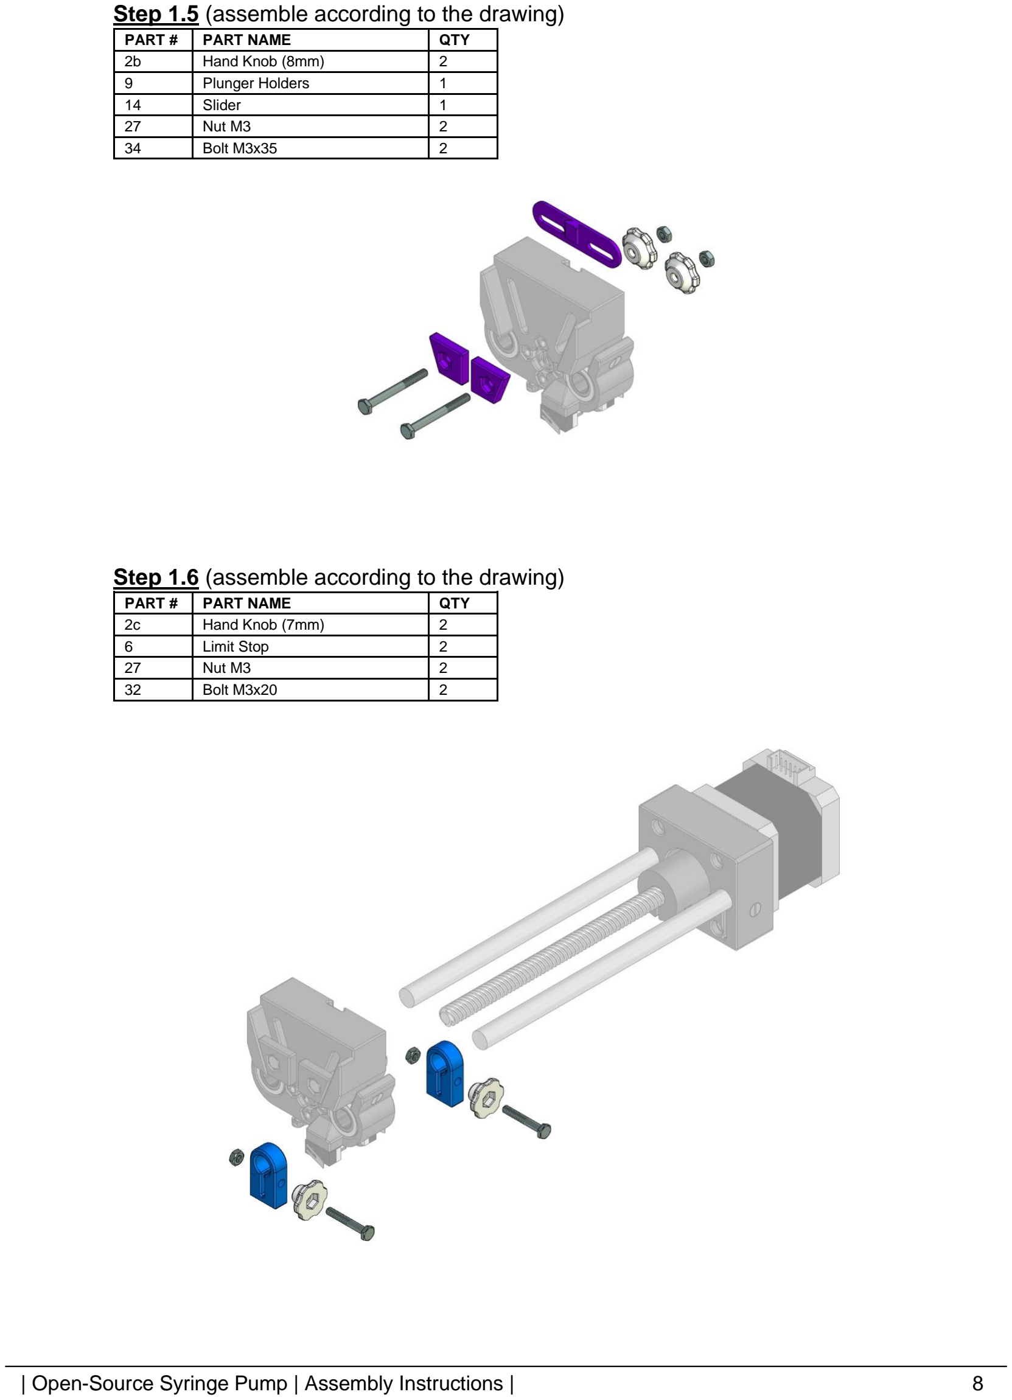
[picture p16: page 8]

Step 1.5 (assemble according to the drawing)
PART # | PART NAME | QTY
2b | Hand Knob (8mm) | 2
9 | Plunger Holders | 1
14 | Slider | 1
27 | Nut M3 | 2
34 | Bolt M3x35 | 2
Step 1.6 (assemble according to the drawing)
PART # | PART NAME | QTY
2c | Hand Knob (7mm) | 2
6 | Limit Stop | 2
27 | Nut M3 | 2
32 | Bolt M3x20 | 2

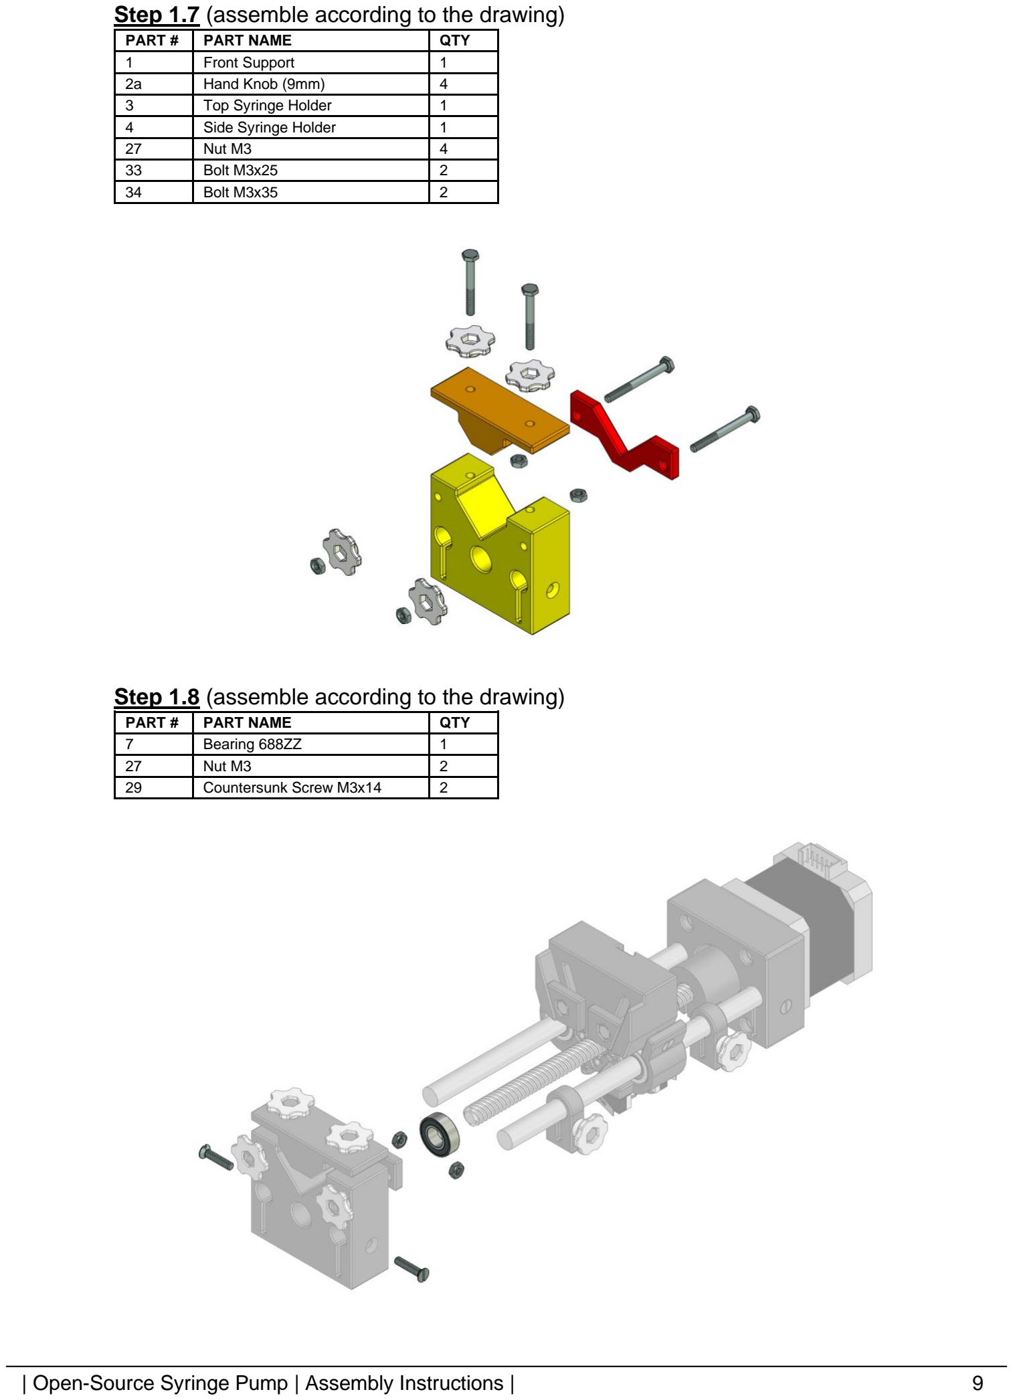
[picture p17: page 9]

Step 1.7 (assemble according to the drawing)
PART # | PART NAME | QTY
1 | Front Support | 1
2a | Hand Knob (9mm) | 4
3 | Top Syringe Holder | 1
4 | Side Syringe Holder | 1
27 | Nut M3 | 4
33 | Bolt M3x25 | 2
34 | Bolt M3x35 | 2
Step 1.8 (assemble according to the drawing)
PART # | PART NAME | QTY
7 | Bearing 688ZZ | 1
27 | Nut M3 | 2
29 | Countersunk Screw M3x14 | 2

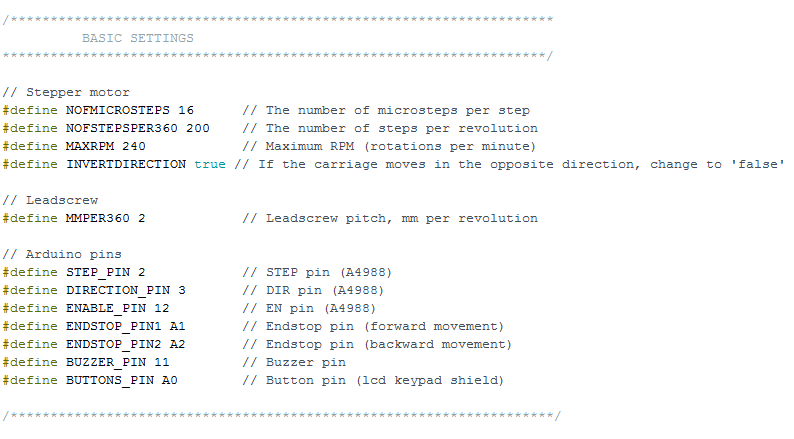
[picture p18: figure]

Step 2.1 (if necessary, change the basic settings in the Arduino sketch)
Step 2.2 (upload sketch to Arduino) Detailed instructions are available at this link. (https://www.arduino.cc/en/main/howto)
Step 2.3 (solder wires and crimp connectors, refer to electrical circuit)
PART # | PART NAME | QTY
22 | Arduino UNO | 1
26 | Active Buzzer (D=12mm) | 1
37 | Dupont Connector (Female) | 6
38 | Dupont Connector (Male) | 3
39 | Dupont Housing (3P) | 2
40 | Connector Wires | –

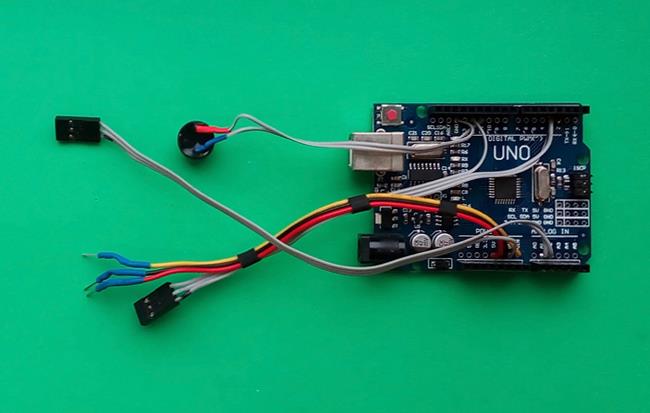
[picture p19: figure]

Step 2.4 (solder wires and crimp connectors, refer to electrical circuit)
PART # | PART NAME | QTY
11 | Endstop Switch | 2
38 | Dupont Connector (Male) | 3
39 | Dupont Housing (3P) | 1
40 | Connector Wires | –

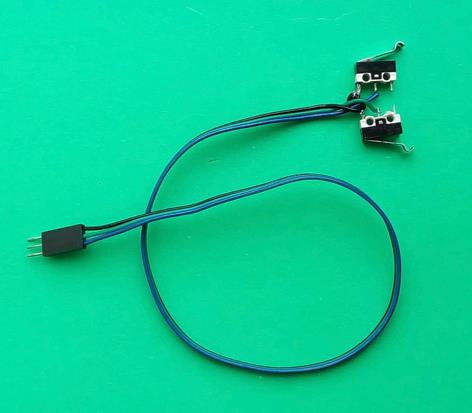
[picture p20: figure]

Step 2.5 (plug A4988 driver into the shield and set all DIP switches to ON)
PART # | PART NAME | QTY
24 | Stepper Motor Driver (A4988) | 1
25 | Control Shield for A4988 | 1

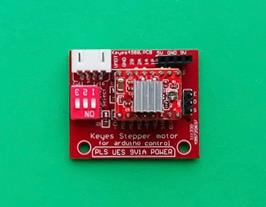
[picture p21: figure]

Step 2.6 (set output current limit on A4988) Detailed instructions are available at this link. (https://howtomechatronics.com/tutorials/arduino/how-to-control-stepper-motor-with-a4988-driver-and-arduino/)

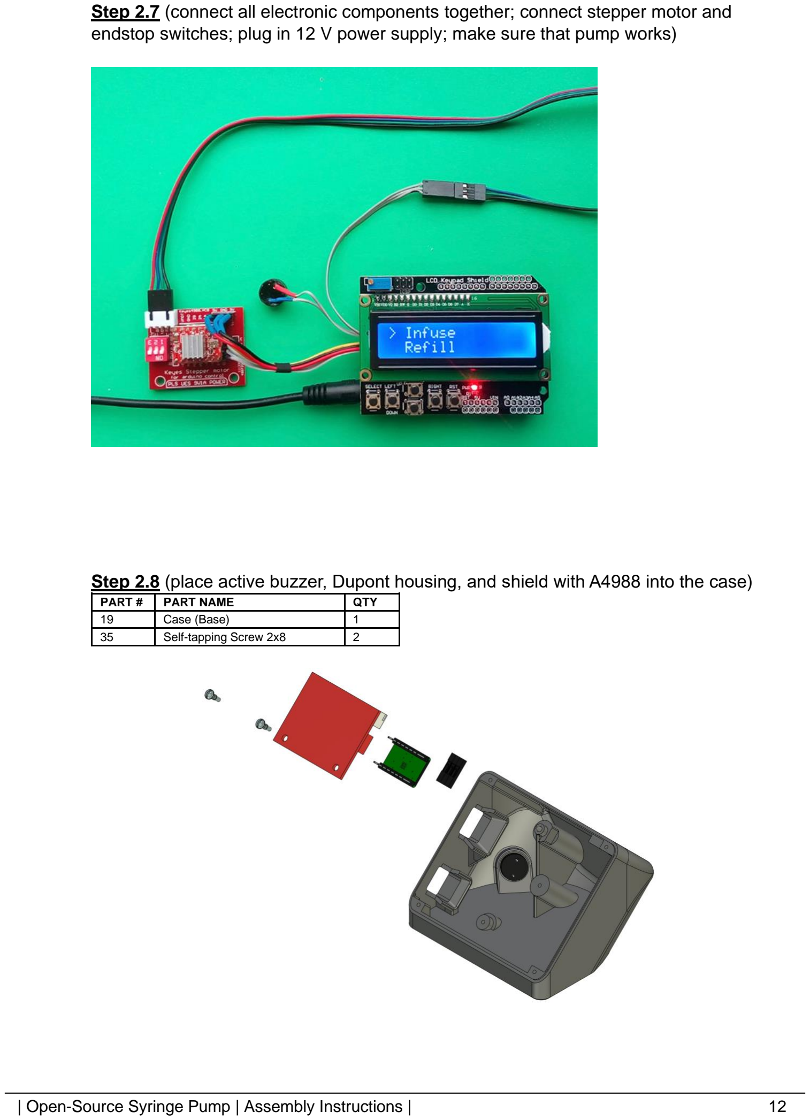
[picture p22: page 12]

Step 2.7 (connect all electronic components together; connect stepper motor and endstop switches; plug in 12 V power supply; make sure that pump works)
Step 2.8 (place active buzzer, Dupont housing, and shield with A4988 into the case)
PART # | PART NAME | QTY
19 | Case (Base) | 1
35 | Self-tapping Screw 2x8 | 2

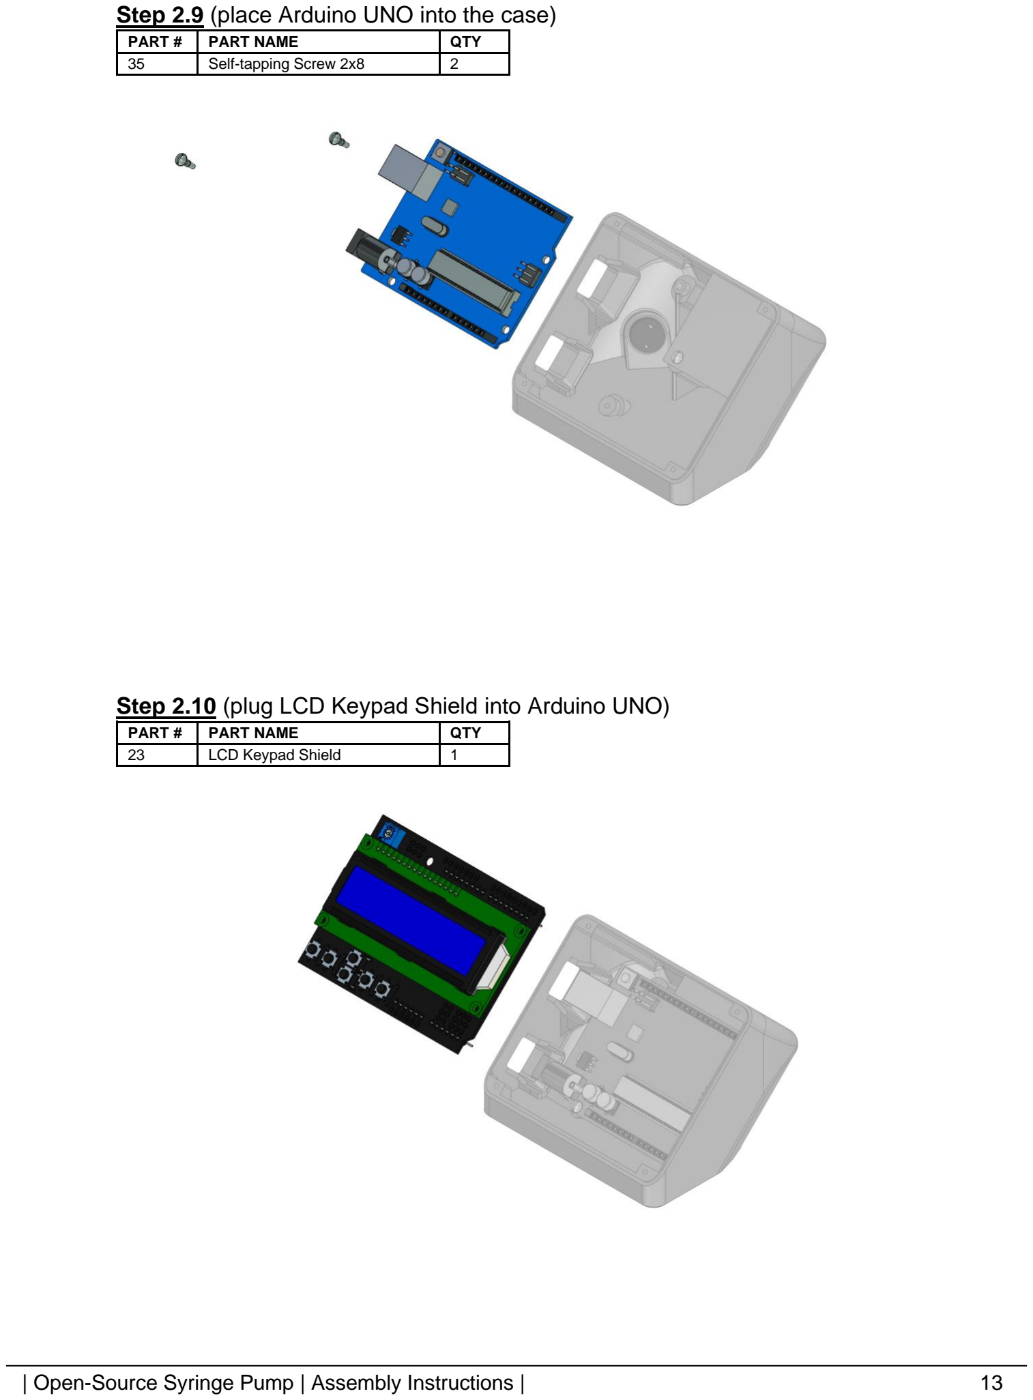
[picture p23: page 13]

Step 2.9 (place Arduino UNO into the case)
PART # | PART NAME | QTY
35 | Self-tapping Screw 2x8 | 2
Step 2.10 (plug LCD Keypad Shield into Arduino UNO)
PART # | PART NAME | QTY
23 | LCD Keypad Shield | 1

Step 2.11 (install buttons and top cover)
PART # | PART NAME | QTY
20 | Case (Cover) | 1
21 | Buttons | 1
36 | Self-tapping Screw 2x10 | 4

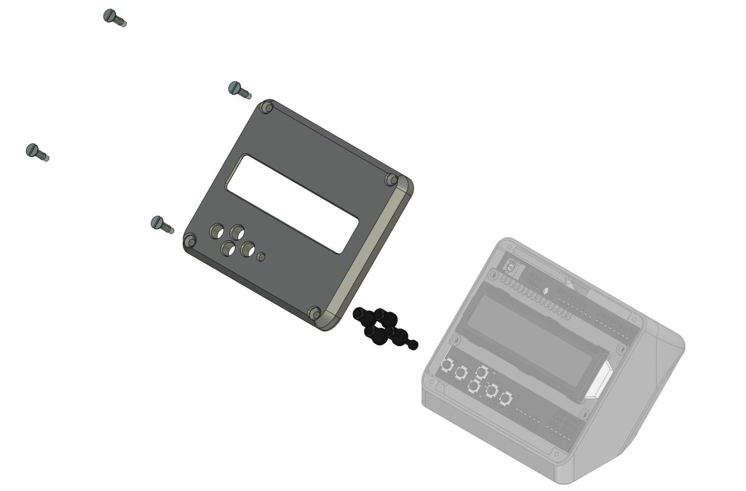
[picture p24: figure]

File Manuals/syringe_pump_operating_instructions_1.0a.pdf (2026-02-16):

# Open-Source Syringe Pump

(developed by Andrey Samokhin in 2018)


# Operating Instructions

(Version 1.0a)

STL-files and "firmware" are available at http://www.mass-spec.ru/projects/diy/syringe_pump/eng/
Project files are distributed under CC BY-SA 4.0 license

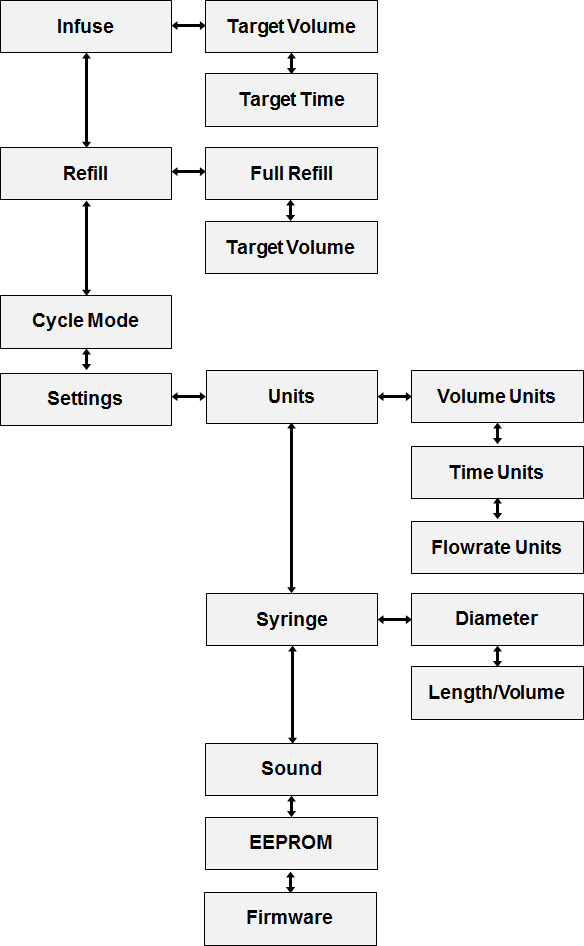
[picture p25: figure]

| Open-Source Syringe Pump | Operating Instructions | | 2

Navigation
Press ▲ or ▼ button to select a menu item.
Press ► button to enter submenu or to perform/confirm action. Press ◄ button to go back or to cancel action.

Fig. 1. Control buttons

Changing value
Press ▼ button to enter setting mode.
Press (or hold) ► or ◄ button to select a digit.
Press (or hold) ▲ or ▼ button to modify selected digit.
To confirm change press ► button several times until you exit setting mode. To cancel change press ◄ button several times until you exit setting mode.

Fig. 2. Menu structure

Left

Right
Down

Up

Reset

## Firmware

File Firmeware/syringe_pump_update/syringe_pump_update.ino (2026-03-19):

/********************************************************************
  Open-Source Syringe Pump
  https://www.mass-spec.ru/projects/diy/syringe_pump/eng/
  Original author: Andrey Samokhin
  Original release: Mar 1, 2020
  Original version: 0.9a

  ----------------------------------------------------------------
  MODIFICATIONS BY: Flavio Mourao
  DATE:             Jan 08 2026
  BASED ON:         syringe_pump_0_9a.ino
  ----------------------------------------------------------------

  CHANGE 1 — Lead screw pitch updated (MMPER360)
    The default 2 mm/revolution lead screw was replaced (optional) by a 0.6 mm/revolution lead screw. This reduces linear displacement
    per motor step, resulting in smoother and more precise motion during microinjection procedures.

  CHANGE 2 — Manual Positioning Mode added (JOG CONTROL)
    A new "Positioning" entry was added to the main menu, accessible between "Cycle Mode" and "Settings".

    Button mapping inside Positioning mode:
      UP    -> forward movement (while held)
      DOWN  -> backward movement (while held)
      LEFT  -> exit and return to main menu
      RIGHT -> reset relative position counter to 0 mm

    Features:
      - Movement occurs only while a button is held
      - Two speeds depending on press duration:
          Short press  -> fine / slow positioning
          Long press   -> coarse / fast positioning
      - Stepper driver is enabled only during movement
      - Audible beep when a mechanical endstop is reached
      - Real-time display of relative displacement in millimeters

    Intended use: manual syringe alignment and fine positioning prior to microinjection procedures.

  CHANGE 3 — Startup screensaver message customized
    The original "OpenSP 0.9 / www.mass-spec.ru" splash screen was replaced with a custom message.

  CHANGE 4 — Start confirmation dialog added (confirmStart)
    A new confirmStart() function was added to require user confirmation before any pumping operation begins.
    The LCD displays "Ready to Start? Yes or No" with RIGHT to confirm and LEFT to cancel. pumpSingly() was updated to call this
    function before proceeding.

  CHANGE 5 — Rounding correction in calculateActualValue()
    In the original code, FLOWRATE and VOLUME computed values were assigned to uint32_t via direct cast (truncation). This has been
    replaced with proper rounding (+ 0.5 before cast), reducing cumulative stepping errors and improving dispensed volume accuracy.

********************************************************************/

#include <LiquidCrystal.h>
#include <EEPROM.h>

/********************************************************************
          BASIC SETTINGS
********************************************************************/

// Stepper motor
#define NOFMICROSTEPS 16      // The number of microsteps per step
#define NOFSTEPSPER360 200    // The number of steps per revolution
#define MAXRPM 240            // Maximum RPM (rotations per minute)
#define INVERTDIRECTION true  // If the carriage moves in the opposite direction, change to 'false'

// Leadscrew
//#define MMPER360 2            // Leadscrew pitch, mm per revolution -- CHANGE 1: original value commented out (default = 2 mm/rev)
#define MMPER360 0.6            // Leadscrew pitch, mm per revolution -- CHANGE 1: replaced with 0.6 mm/rev for smoother microinjection

// Arduino pins
#define STEP_PIN 2            // STEP pin (A4988)
#define DIRECTION_PIN 3       // DIR pin (A4988)
#define ENABLE_PIN 12         // EN pin (A4988)
#define ENDSTOP_PIN1 A1       // Endstop pin (forward movement)
#define ENDSTOP_PIN2 A2       // Endstop pin (backward movement)
#define BUZZER_PIN 11         // Buzzer pin
#define BUTTONS_PIN A0        // Button pin (lcd keypad shield)

/********************************************************************/



#define DEBOUNCEDELAY 50
#define LONGPRESSDELAY 450
#define AUTOCHANGINGDELAY 300

#define NITEMS 44  // CHANGE 2: incremented from 43 to 44 to accommodate the new Positioning menu entry

#define LINK2S 12
#define LINK2E 13
#define LINK2V 20
#define LINK2T 21
#define LINK2F 22
#define LINK2DIA 41
#define LINK2LPV 42

LiquidCrystal lcd(8, 9, 4, 5, 6, 7);

struct MenuItem
{
  uint8_t button[4];
  uint8_t type;
  char *text;
  uint8_t address;
  uint32_t value;
};

enum listOfButtons {RIGHT, UP, DOWN, LEFT, SELECT, NA};
enum listOfButtonStates {RELEASE, SHORTPRESS, MEDIUMPRESS, LONGPRESS};
enum listOfPrograms {CHANGEVALUE = 200, SELECTFROMLIST, INFUSEVOLUME, INFUSETIME, REFILLVOLUME, REFILLFULL, CYCLEMODE, FIRMWAREINFO,POSITIONING};  // CHANGE 2: added POSITIONING to the program enum
enum listOfItemTypes {TEXT, LIST, VOLUME, TIME, FLOWRATE, LENGTHPERVOLUME, DIAMETER};

const char firmwareInfo[] = "0.9a";
const uint16_t volumeDivider[2] = {1000, 1};
const uint16_t timeDivider[3] = {1, 60, 3600};
const uint16_t flowrateDivider[4] = {60000, 1000, 60, 1};
const float stepsPERmm = NOFSTEPSPER360 / MMPER360;

MenuItem items[NITEMS];
uint8_t lastButton = NA;
uint8_t buttonState = RELEASE;
uint32_t buttonPressTime = 0;
uint8_t currentItem = 1;
float coef;
uint8_t endStopPin;
volatile uint32_t ustepCounter;
uint32_t ustepCounterLimit;
long positioning_uSteps = 0;  // CHANGE 2: global microstep counter for Positioning mode

uint32_t getValue(uint8_t itemNo);
void changeValue();
void setValue(uint8_t itemNo, uint8_t digits[8]);
void selectFromList();
void calculateActualValue(uint8_t itemNo);
void recalculateSyringe(uint8_t itemNo);
void printScreen();
void printUnits();
void printFirmwareInfo();
void printTimeAndVolume(uint16_t pumpingTime, uint32_t pumpingVolume);
void showScreensaver();
void readFromEEPROM(uint8_t itemNo);
void writeToEEPROM(uint8_t itemNo);
void getButtonState();
uint16_t valueDivider (uint8_t n);
uint8_t getElementNo(uint8_t linkToList);
void waitingForButton(uint8_t buttonCode, uint8_t itemNo);
void beep (uint16_t delayOn = 15, uint16_t delayOff = 100);
bool checkEndstop(int8_t pumpingDirection);
void infuseVolume();
void infuseTime();
void refillVolume();
void refillFull();
bool confirmStart();  // CHANGE 4: forward declaration for the new confirmation dialog function
void pumpSingly(int8_t pumpingDirection, uint32_t flowrate, uint32_t volume);
void pumpContinuously();
uint8_t pump(uint32_t flowrate, uint32_t volume);
void positioningMode();  // CHANGE 2: forward declaration for the new positioningMode() function


/********************************************************************
  setup
********************************************************************/
void setup()
{
  lcd.begin(16, 2);

  pinMode(STEP_PIN, OUTPUT);
  pinMode(DIRECTION_PIN, OUTPUT);
  pinMode(ENABLE_PIN, OUTPUT);
  pinMode(ENDSTOP_PIN1, INPUT_PULLUP);
  pinMode(ENDSTOP_PIN2, INPUT_PULLUP);
  pinMode(BUZZER_PIN, OUTPUT);

  digitalWrite(ENABLE_PIN, HIGH);

  items[1]  = {5, 0, 2, 0, TEXT, "Infuse"};
  items[2]  = {7, 1, 3, 0, TEXT, "Refill"};
  items[3]  = {9, 2, 4, 0, TEXT, "Cycle Mode"};
  items[4]  = {10, 3, 0, 0, TEXT, "Settings"};
  items[5]  = {15, 0, 6, 1, TEXT, "Target Volume"};
  items[6]  = {16, 5, 0, 1, TEXT, "Target Time"};
  items[7]  = {17, 0, 8, 2, TEXT, "Full Refill"};
  items[8]  = {18, 7, 0, 2, TEXT, "Target Volume"};
  items[9]  = {19, 0, CHANGEVALUE, 3, FLOWRATE, "infuse flow:", 1, 120000000};
  items[10] = {20, 0, 11, 4, TEXT, "Units"};
  items[11] = {23, 10, 12, 4, TEXT, "Syringe"};
  items[12] = {25, 11, 13, 4, LIST, "Sound", 2};
  items[13] = {27, 12, 14, 4, LIST, "EEPROM", 3};
  items[14] = {FIRMWAREINFO, 13, 0, 4, TEXT, "Firmware"};
  items[15] = {29, 0, CHANGEVALUE, 5, VOLUME, "volume:", 4, 1000000};
  items[16] = {30, 0, CHANGEVALUE, 6, TIME, "time:", 5, 60000};
  items[17] = {REFILLFULL, 0, CHANGEVALUE, 7, FLOWRATE, "flowrate:", 6, 2000000};
  items[18] = {31, 0, CHANGEVALUE, 8, VOLUME, "volume:", 7, 1000000};
  items[19] = {CYCLEMODE, 0, CHANGEVALUE, 9, FLOWRATE, "refill flow:", 8, 2000000};
  items[20] = {32, 0, 21, 10, LIST, "Volume Units", 9};
  items[21] = {34, 20, 22, 10, LIST, "Time Units", 10};
  items[22] = {37, 21, 0, 10, LIST, "Flowrate Units", 11};
  items[23] = {41, 0, 24, 11, TEXT, "Diameter"};
  items[24] = {42, 23, 0, 11, TEXT, "Length/Volume"};
  items[25] = {SELECTFROMLIST, 0, 26, 12, TEXT, "on"};
  items[26] = {SELECTFROMLIST, 25, 0, 12, TEXT, "off"};
  items[27] = {SELECTFROMLIST, 0, 28, 13, TEXT, "on"};
  items[28] = {SELECTFROMLIST, 27, 0, 13, TEXT, "off"};
  items[29] = {INFUSEVOLUME, 0, CHANGEVALUE, 15, FLOWRATE, "flowrate:", 12, 2000000};
  items[30] = {INFUSETIME, 0, CHANGEVALUE, 16, FLOWRATE, "flowrate:", 13, 2000000};
  items[31] = {REFILLVOLUME, 0, CHANGEVALUE, 18, FLOWRATE, "flowrate:", 14, 2000000};
  items[32] = {SELECTFROMLIST, 0, 33, 20, TEXT, "mL"};
  items[33] = {SELECTFROMLIST, 32, 0, 20, TEXT, "uL"};
  items[34] = {SELECTFROMLIST, 0, 35, 21, TEXT, "s"};
  items[35] = {SELECTFROMLIST, 34, 36, 21, TEXT, "min"};
  items[36] = {SELECTFROMLIST, 35, 0, 21, TEXT, "h"};
  items[37] = {SELECTFROMLIST, 0, 38, 22, TEXT, "mL/s"};
  items[38] = {SELECTFROMLIST, 37, 39, 22, TEXT, "mL/min"};
  items[39] = {SELECTFROMLIST, 38, 40, 22, TEXT, "uL/s"};
  items[40] = {SELECTFROMLIST, 39, 0, 22, TEXT, "uL/min"};
  items[41] = {0, 0, CHANGEVALUE, 23, DIAMETER, "diameter:", 15, 11284};
  items[42] = {0, 0, CHANGEVALUE, 24, LENGTHPERVOLUME, "length/volume:", 16, 10000};
  items[43] = {POSITIONING, 0, 0, 0, TEXT, "Positioning"};  // CHANGE 2: new Positioning menu item (index 43)
  items[3].button[DOWN] = 43;    // CHANGE 2: "Cycle Mode" now navigates DOWN to "Positioning"
  items[43].button[UP]  = 3;     // CHANGE 2: "Positioning" navigates UP to "Cycle Mode"
  items[43].button[DOWN] = 4;    // CHANGE 2: "Positioning" navigates DOWN to "Settings"
  items[4].button[UP]    = 43;   // CHANGE 2: "Settings" navigates UP to "Positioning"
  items[4].button[DOWN]  = 1;    // CHANGE 2: "Settings" navigates DOWN to "Infuse" (menu wrap-around)
  items[1].button[UP]    = 4;    // CHANGE 2: "Infuse" navigates UP to "Settings" (menu wrap-around)

  for (uint8_t i = 1; i < NITEMS; i++)
  {
    if (items[i].type != TEXT) readFromEEPROM(i);
  }

  recalculateSyringe(LINK2DIA);
  beep();
  showScreensaver();
}



/********************************************************************
  loop
********************************************************************/
void loop()
{
  uint8_t nextItem;
  getButtonState();
  if (buttonState == SHORTPRESS && lastButton != SELECT)
  {
    buttonState = MEDIUMPRESS;

    nextItem = items[currentItem].button[lastButton];
    if (nextItem != 0 && nextItem < 200)
    {
      currentItem = nextItem;
      printScreen();
    }
    else if (nextItem == CHANGEVALUE) changeValue();
    else if (nextItem == SELECTFROMLIST) selectFromList();
    else if (nextItem == INFUSEVOLUME) infuseVolume();
    else if (nextItem == INFUSETIME) infuseTime();
    else if (nextItem == REFILLVOLUME) refillVolume();
    else if (nextItem == REFILLFULL) refillFull();
    else if (nextItem == CYCLEMODE) pumpContinuously();
    else if (nextItem == FIRMWAREINFO) printFirmwareInfo();
    else if (nextItem == POSITIONING) positioningMode();  // CHANGE 2: dispatch to positioningMode() when selected from menu
  }
}



/********************************************************************
  getValue
********************************************************************/
uint32_t getValue(uint8_t itemNo)
{
  uint16_t divider = valueDivider(items[itemNo].type);
  uint8_t lastDigitIncrement = 0;
  if ( uint16_t(items[itemNo].value % divider) > divider / 2) lastDigitIncrement = 1;

  if (items[itemNo].value / divider > 99999999)
  {
    items[itemNo].value = divider * 99999999;
    return 99999999;
  }
  else return (items[itemNo].value / divider) + lastDigitIncrement;
}
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
